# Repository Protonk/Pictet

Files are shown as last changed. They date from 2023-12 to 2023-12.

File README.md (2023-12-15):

# Pictet's Experiment

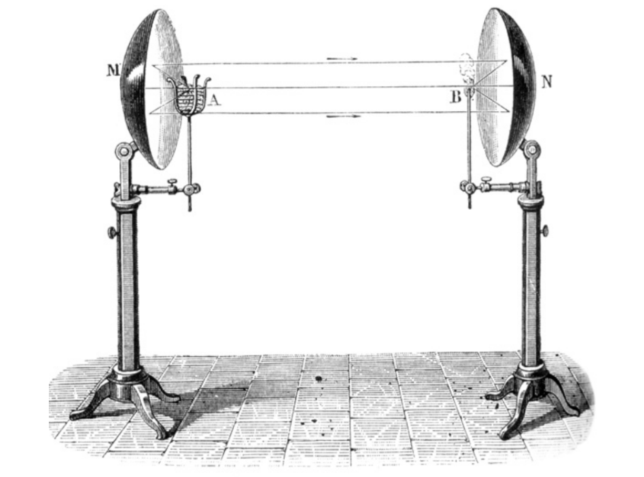
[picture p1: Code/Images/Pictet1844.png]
A lithograph of two parabolic mirrors on stands facing each other. The focus of one mirror has a basket of coals, the other kindling 1844 Apparatus


We are students of human-computer interaction who feel that speculation is important in the classroom. Speculating, failing, and then learning from our failure is how we innovate and advance as a society and grow as people. Science classrooms are important places for students to reason and speculate about the world, but sometimes they can feel intimidating to speak up in. We wanted to design a science demonstration focused on creating space for students to speculate about the outcome without fear of being wrong. Because we are not physicists or science teachers, rather than devising a new experiment, we decided to lift one out of some obscurity in the history of thermodynamics and show that through user research this experiment was still viable for classroom learning today, more than 200 years after it was first performed: [Pictet's Experiment](https://en.wikipedia.org/wiki/Pictet%27s_experiment), which showed the reflection of radiative heat by mirrors and the **apparent** reflection of cold.

We chose this experiment because despite a simplicity that allows it to be shown in a middle-school classroom, it can be surprising even to working physicists and students with experience with physics and heat transfer. It can accompany a discussion of blackbody radiation, visible and invisible light on the electromagnetic spectrum, or merely a discussion of what makes things hot and cold.

To accompany this demonstration we provide instructional materials in different modalities, designed through iterative user and concept testing of students' inclinations to speculate and reason about the outcomes. These are integrated into a short lesson plan with suggestions for staging and key questions to ask. We also offer guidance on how to implement the lesson, materials to support student engagement, and evidence for the impact of a learner seeing the demonstration for the first time.

## Contents

This project contains a capsule lesson plan appropriate for middle and high school science classrooms with a heat transfer component. The plan includes directions for constructing and conducting a demonstration, key concepts and questions for students, as well as a variety of optional discussion questions to allow the lesson to be tailored for student level and time allotted.

This lesson plan is released under a public domain license. Anyone may freely copy, modify or re-use the material we have created.

If you want to demonstrate this experiment in your classroom you may follow the links below.

- [Lesson Plan and Teacher's Guide](/Lesson%20Plan/Lesson%20Plan.pdf)
- [Experimental and Material Setup Instructions](/Lesson%20Plan/Experimental%20and%20Material%20Setup%20Instructions.pdf)
- [Resources for replication](/Excerpts/)

Read on for more information about why and how we put the lesson plan together.

## Why this project?

We did not want to make an app or design a change to how classrooms work. Science teachers don't need us or technology to help them understand that speculation is important. Classic experiments with [pendulums](https://www.aps.org/programs/outreach/physicsquest/past/swinging.cfm) are widely used to help students reason and speculate about concepts like mass, and science educators have been writing for [some time](https://pubs.acs.org/doi/10.1021/ed013p166)  about the importance of demonstration in the classroom.

We wanted to take advantage of our background as designers and researchers as well as the opportunity we had to conduct user and concept testing with students in order to attack a problem of narrow scope: a lesson plan that helps prompt speculation and inquiry in students, where the key stakeholders are limited to instructors themselves. This allowed us to focus on stakeholder needs and produce a solution that could be deployed today just as we have designed it.

### Doing research so teachers don't have to

Although Pictet's experiment was regularly demonstrated to students and included in at least one popular teacher's guide in the 19th century, someone today is likely to find it (if they find it at all) recorded as a curious footnote in the history of physics. Sandwiched between discussions of "frigorific rays" and "phlogiston", its value as a teaching tool is obscured. Further, finding pragmatic information about the demonstration such as suitable materials or valuable practices is a challenge and requires access to and a willingness to read paywalled journal articles for an uncertain benefit.

We suspected that middle and high school teachers were unlikely to see this as a good use of their time and we aimed much of our early secondary research at lifting Pictet's experiment out of this historical frame and collecting information about its use as a teaching tool into one place. This notion turned into our idea for our final deliverable for this project: a lesson plan. With our lesson plan, an instructor who discovers the experiment in one of those footnotes mentioned above and searches for more information will have, readily available, enough information to determine both the value of demonstrating it to their classroom and practical information about how to do so.

Teachers often have very few chances to test out additions to the classroom, but we could test and iterate on this specific goal with users throughout the design process. This allowed us to bring to bear our experience with user testing and validation to the problem of designing a lesson plan.

## Limitations

Because our solution is aimed at middle and high school teachers, the best user population is students of those ages. However, minors are always considered a vulnerable population for research (including class projects!) so all work must proceed through an Institutional Review Board (IRB). Given that the time frame for our project was less than 10 weeks, we moved forward by testing important elements of the lesson on a proxy–university students. On top of this limitation was a further one, we could not test users in an environment close to what we expected the lesson plan to be used in: a classroom. Our user testing was built around the recruitment of individuals for interviews and demonstrations.

Given these limitations, we approached user testing with the aim to first validate that our demonstration could create a space for speculation by the user and then to observe how user responses changed as the demonstration evolved. As the project went on and we continued to iterate on our prototypes, we put much of what is the lesson plan in front of users for validation and concept testing. However, the whole of the lesson plan could not be tested in the classroom environment we expect to see it used in.

Finally, we are not students of physics or working physicists. We feel experimental demonstrations of scientific knowledge must be carried out by scientists and non-scientists alike in order to broaden the scope and character of scientific knowledge. Our work in building the experiment and attending carefully to the user's behavior can offer lessons for science educators, not least of which is drawing attention to an experiment we believe has been unfairly neglected.

### Who we spoke with

We not only needed to read up on the experiment, but conduct user research as well. For example, our secondary research showed that Pictet's experiment was able to puzzle and surprise even well-educated physicists at the time, but we did not know if students today would react the same way. Would students who live in the modern world of heat lamps and infrared cameras still have their intuitions challenged? Did this experiment in fact create a space where students are able to speculate freely?

To answer these questions and others, we conducted user interviews with key stakeholders and moderated user testing with various iterations of prototypes, both of which we will explain in detail below.

#### Science Teachers

Our stakeholders for this project–the people who we hope will take up this lesson plan–are middle and high school STEM teachers. We conducted semi-structured interviews with three teachers via Zoom. One teaches in a well-resourced private school, one in a home-school co-op, and one via community science education programs. They were asked various questions regarding their perspective on demonstrating science experiments in front of students and general thoughts about the best way to create a space where students feel comfortable to speculate openly without the fear of being wrong or judged by their peers or teachers.

#### Student interviews

User interviews with undergraduate and graduate students were conducted as semi-structured interviews at the student union building at a local university. They consisted of questions asking about general perspectives and experiences about science classes and also specific questions regarding how different situations impacted their ability to speculate freely within the classroom. While we could not interview middle or high school students for our work, speaking with a mix of students inside and outside of STEM fields helped us understand how to consider students as a user group in general, rather than just speaking with instructors.

#### Capsule demonstrations

Once we conducted initial interviews with students, we prototyped virtual and in-person demonstrations with university students at the student union. Each demonstration included a short pre- and post- interview which we used to evaluate the effectiveness of the staging and presentation of the lesson.

#### Results

Through the synthesis and analysis of our qualitative data collected from the user and stakeholder interviews, the common themes and trends that emerged helped guide major design choices. For instance, our initial goal was to replicate the experiment and produce only a video to be shown in the classroom. While some of our stakeholders wanted options of how to demonstrate experiments to the class including simply showing a video, students prefer live demonstrations or hands-on experiments as opposed to watching a video. One student noted a common sentiment, saying "if this is something that can be demonstrated in person it would definitely be more interesting." This along with other discussions with students who preferred seeing and interacting with a demonstration even if they were not responsible for performing it, led us to produce a lesson plan with instructions on guiding the demonstration.

Another way that we involved the input of the interviews was with the worksheet handout that we included in the lesson plan. One teacher explained their philosophy of trying "to get students to make a prediction first as a way to engage more deeply with what's about to happen, especially if it's a common misconception that we are trying to reveal." This sentiment was echoed by a student who shared how they are: "[more comfortable with] 'write down what you think would happen' or make it anonymous [type of situations]." With this in mind, we crafted a hypothesis worksheet that had the students anonymously write down their hypothesis of what they thought was going to happen in the demonstration and why. Then after the demonstration, on the back of the same worksheet, it asks the students to explain what actually happened and what if anything was surprising to them.

## Takeaways

When we started on this project, lots of things were uncertain to us. We did not know whether or not students today would find the experiment counterintuitive or if it would provide space for them to speculate about the phenomena at work. We also did not know if we could recreate the experiment ourselves; how to integrate our secondary research about inquiry-based learning with our user research; or whether or not low and medium-fidelity prototypes would give good approximations to what we wanted to test.

Our first major takeaway from the project was that low-fidelity prototypes can work well in this space. Users, especially those we engaged in person, had less difficulty than we imagined understanding papercraft representations of the experiment, allowing us to effectively perform concept and user testing early on in the design process. Virtual demonstrations proved less effective in terms of eliciting speculation but still provided important feedback which we incorporated into our design.

Another takeaway came from the nature of the user tests we were able to perform. We discovered in our user and stakeholder interviews that students preferred to give speculations and hypotheses first in private or in small groups before volunteering these ideas to the whole class. Motivated by this, we developed worksheets to go along with the lesson plan where students can record speculation privately. However, our user testing was almost exclusively one-on-one, and users were understandably reluctant to write detailed feedback during user tests–preferring to offer it verbally. This meant that while we have good evidence from user and stakeholder interviews on the value of private, written speculation in these scenarios, we were limited in how we could assess our solution here.

## Future work

The limitations noted above offer clear signs for future work. Our next steps for the lesson plan are:

- Seek out Institutional Review Board (IRB) approval to demonstrate and assess the response of our intended user group (middle or high school students) in a classroom environment.
- In collaboration with stakeholders, develop assessments for student learning during the demonstration. As one of our stakeholders noted, "Most of the learning is answering post-lab questions."

Aside from these major improvements, our lesson plan is available here on GitHub, where comments and suggested changes can be continuously integrated. The lesson plan and associated materials are shared under a free license so anyone can copy, adapt, and re-use what we have created for their classrooms.

Contributions are welcome!

## Just who is we?

* This project is the work of [Adam Hyland](https://adampunk.com) and [Daniel Teramoto](https://www.linkedin.com/in/daniel-teramoto/), students at the Human Centered Design and Engineering department of the University of Washington.

## Acknowledgements

This project was produced in Dr. Daniela Kim's User Centered Design course. We are grateful for her feedback and support as well as the support of our awesome TA Brian Kinnee. Thanks also to Dr. Brock Craft for assistance with fabrication.

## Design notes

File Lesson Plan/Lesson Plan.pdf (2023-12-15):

# The Third Heat: Pictet’s Experiment

## Intro

Let us think for a moment about how heat appears to us as a sensation. We can feel what we know of as conduction–A hand on a hot pan. We can feel convection–a fire warming a room. But we also sense a different kind of heat. When opening a furnace door we feel heat IMMEDIATELY, much faster than air molecules around the furnace could reach us.

We also feel the heat of the sun. Stepping out of full shade on a hot day makes things immediately hotter. How does that work? Is that energy we experience part of the light we can see? The sun is certainly bright, and so is a hot furnace. But plenty of hot things don’t emit light. Humans are pretty warm and we don’t visibly glow. Neither does a hot pan one might reach for.

Let’s travel back in time to 1790. We don’t know that the light we see is just a tiny slice of a broad spectrum of energy, most of which is invisible to us. It is ten years before the first bit of this spectrum outside our visual experience will get isolated and examined scientifically.

What we have is a suspicion that beyond conduction (touching that hot pan), and convection (feeling the heat of a fire roil through the air), there is a third heat, one which travels quickly like light. To turn this suspicion into knowledge, scientists turn to experiments. We are going to conduct one today like it would have been done 230 years ago.

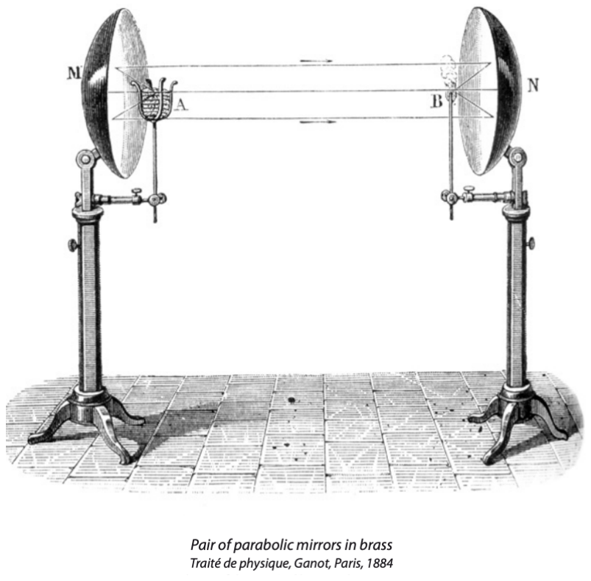
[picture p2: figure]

## The Science Behind Reflection of Heat

Pictet’s experiment is the name given to a series of experiments performed in 1790 by Marc-Auguste Pictet which demonstrated radiative heat transfer and reflection of radiated heat from objects that were not visibly glowing, ten years before the isolation of infrared light from sunlight and half a century before modern theories of black-body radiation were developed.

After measuring an increase in temperature from the reflected heat of an object, a colleague suggested to

Pictet that he insert a very cold object and see what happens. Snow was brought into the laboratory and placed where the hot object had been. To Pictet’s surprise, the temperature of the thermometer went down.

Some scientists at the time struggled with this result because they held a misconception noted in students of heat transfer today, that cold objects–those which feel cold to the touch–emit or radiate coldness akin to how we sense radiant heat from hot objects. Others, who knew that cold was the absence of heat, incorrectly inferred from this that the temperature should remain the same, and had to update their intuition.

The experiment was a way to move beyond apprehending radiant heat with our senses to measuring it with tools. What we would now call heat flux from an object could be reflected by mirrors, and focused following the same rules of optics that visible light did. Infrared cameras like those on the James Webb Space Telescope that today help us peer further into the past than we have seen before operate on principles demonstrated here.

### Suggested placement of the lesson

The demonstration of Pictet’s experiment can be useful for a range of students. This lesson plan has been designed to allow instructors the option to teach the material at a variety of levels. While the key question, “how is heat reflected and focused by mirrors” is relatively simple, the questions the demonstration prompts students to ask can be productive even for students with a fair amount of experience in physics.

For middle school science students learning about modes of heat transfer, the demonstration can prompt students to inquire about the role and nature of radiative heat transfer. Those classrooms may choose to skip questions about the determination of the focal point and questions about how much thermal radiation is collected by the mirrors. However, a review of these principles can be achieved without calculus and only some trigonometry

1
. Further, while
heat flux impinges on an area, the discussion can be simplified by considering only a two-dimensional mirror and object setup.

While not covered directly in this lesson plan, asking students to consider different material choices for the hot object can prompt discussions about the relative role of emissivity and reflectivity of objects with respect to radiative heat transfer, a subject with concept inventories have shown to be a common source of student misconceptions.

1 We assume spherical mirrors and only consider objects at the focal point of these mirrors, simplifying the calculations.

## Key Terms

Focal Point: The point at which parallel light rays passing through a lens or reflected from a curved mirror converge, or the point from which they appear to diverge after refraction or reflection by the lens or mirror. Also called the focus or the principal focus.

Concave: Curving inwards. A concave mirror is one in which the reflecting surface is formed from the interior surface of a sphere or paraboloid. For this lesson, we treat all concave mirrors as spherical.

Black-body radiation: Thermal radiation emitted by an ideal, non-reflective object, dependent only on the object’s temperature.

Infrared: Electromagnetic radiation just below the range of visible light. Sometimes referred to as “thermal radiation” or “radiative heat”.

Conduction: The process by which heat is directly transmitted through a substance when there is a difference of temperature or of electrical potential between adjoining regions, without movement of the material.

Convection: Movement caused within a fluid by the tendency of hotter and therefore less dense material to rise, and colder, denser material to sink under the influence of gravity, which consequently results in the transfer of heat.

Radiative heat transfer: Transfer of energy via thermal radiation, i.e., electromagnetic waves. This occurs across a vacuum or any transparent medium (solid, fluid, or gas). Thermal radiation is emitted by all objects at temperatures above absolute zero, due to random movements of atoms and molecules in matter.

## KEY QUESTION:

## How is heat reflected and focused by mirrors?

## Getting Started

The goal of this lesson is for students to understand Pictet’s counterintuitive science experiment first performed in 1790, showing the reflection of radiative heat by mirrors and the apparent reflection of cold. Some main objectives are to encourage the students to be creative, to think like scientists and engineers, and to give them a space where they are free to speculate about the results of the science demonstration without having the pressure of saying their guess in front of their peers.

Materials Needed:
- 2 concave mirrors
- 1 temperature sensing device
- A hot object
- A cold object
- Objects to hold the concave mirrors, thermometer, and heat source in place

If you do not have the exact materials, you can follow our associated experimental setup document which provides budget-friendly alternatives for how to demonstrate the experiment best.

### Demonstration Setup

See the associated experimental setup document.

## Safety

The experiment uses hot and cold objects. The simplest hot object to use is a candle–precautions for handling open flame are required. A glass of ice water is sufficient for a cold object, but the effect will be more dramatic the colder the object is. The use of dry ice or liquid nitrogen to cool a metal object requires precautions in the classroom.

### Before starting the demonstration with students, consider these questions

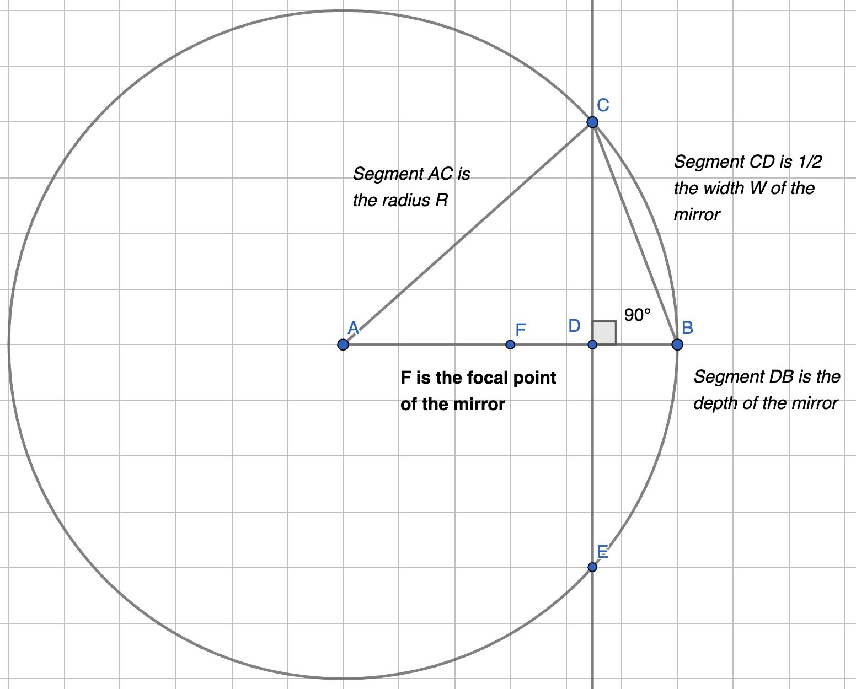
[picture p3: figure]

How do light rays reflect off concave
mirrors?

In setting up and discussing the experiment, discussing how visible light is reflected by mirrors can motivate where the objects and thermometer are placed relative to the mirrors. For concave mirrors, light radiating from the focal point of a mirror will reflect perpendicular to the axis of the mirror. Calculating this focal point, because it comes from these nearly parallel rays, can use the small angle or paraxial approximation, and no calculus or overt trigonometry is needed. The distance of the resulting focal point F is F = R / 2 where R is the radius of the imaginary sphere that the mirror forms a part of.

If a light bulb is placed at the focus of a spherical mirror, a cone of that light is collected in the mirror and reflected in a beam. But the light from which isn’t captured by the beam falls off with the square of the distance from the source. This is how the headlights of a car can shed light at a distance but the same light held in the air would illuminate only a short distance.

What are the ways we can feel the sensation of heat?

This is a broad question that can be answered by students from their experience. Prompt them to think about touching hot objects and feeling the heat of a fire to get them to think about conduction and convection. For radiative heat transfer, this may require some additional prompting. Students may or may not have experience with a furnace or kiln—if they do, ask about how quickly they feel the heat from these objects at a distance. If they do not, prompt them to think about stepping into the sun on a windy day. The heat felt in that scenario cannot be via convection and must come from something else.

Does heat bounce off mirrors like light rays?

This can be posed to almost any student. After discussing the above, prompt students to think about roasting meat or vegetables. We often “tent” a roast by wrapping it in foil. What purpose might this serve? After removing a hot object from the oven, it will cool to room temperature if left alone. Covering the object in foil insulates it. If heat is transmitted via conduction or convection alone, it might serve to wrap an object in paper. Why do people use foil in their kitchens instead?

This question can be extended to a discussion of the characteristics of an object, specifically emissivity and reflectivity. However, for classes that have not discussed these topics, a general discussion can still be valuable.

Does the transfer of “cold” exist separate from the transfer of heat?

The range of human sensation provides an important anchor for understanding the world, but it can mislead us. We tend to think of objects that are warm to the touch as “hot” and those that appear cold as “cold” and students can hold the misconception that this split in sensation means a split in function or behavior.

One way to motivate questions like these can be to hand out cold packs that have just come out of a freezer as well as cold packs that have been allowed to come to room temperature. Objects at room temperature will not cause a strong sensation but cold objects will.

Another way to move this question forward is to have students discuss the implications of a hypothesis that cold objects emit or radiate coldness. If an object “gives off” cold, does a colder object give off more? Does a hot object also give off cold? When might an object stop giving off cold and instead give off heat? Probing questions like these can help students steer themselves to a conclusion that heat transfer occurs across a difference in temperature, rather than being connected to the sensation of hot and cold.

What is black-body radiation?

Where the demonstration is performed with a heated object (not a candle), students can be prompted to inquire about what features of the object aside from its temperature determine the amount of thermal energy transmitted. A “perfect” black-body emitter will give off the maximum amount of energy at a given temperature, while an object painted white will give off far less.

A comparison of those two situations is not the only question that can be posed. One of the key goals of the original experiment was to determine whether or not an object that was not visibly glowing gave off thermal radiation. In the “hot” stage, this can be shown with a hot object, but in the “cold” and “reset” stages, radiation of heat from the thermometer to the environment is observed. Here students can see that something that is roughly room temperature can radiate heat.

### Setting the Stage: Fostering Inquiry-Based Learning

Prior to demonstrating the experiment–either during class or as a take-home assignment beforehand–distribute the attached hypothesis worksheet. The questions ask students to make simple predictions about the behavior of the system during the experiment. The main goal is to get students to advance a prediction and articulate their reasons why they did so.

Once you have the demonstration set up, responses in class work best in small groups. Even though for practical purposes there will likely be only one demonstration in the classroom, student reflection and discussion in groups helps them advance and process speculation about the outcome.

Have the students discuss amidst their group and decide which hypothesis they think is best. Make sure that each group has a spokesperson for their group that can share their hypothesis’ -science happens in community!

Next, have a class discussion where each team reflects to the class their hypothesis and discuss in class the potential consequences of each. After demonstrating the experiment with a hot object, ask groups to review the outcomes and report on how the system behavior deviated from what they expected. Most groups are likely to produce a “correct” answer at this stage–ie a hypothesis that says that the temperature at the sensor will go up with a reasonable explanation as to why.

When you repeat this process with the cold object, answers are more likely to vary both in predicted outcome and rationale.

## Demonstration of the experiment

The demonstration has roughly three stages: hot, reset, and cold.

Pictured is the setup for Pimpas et al. (2017), which recreated the experiment using a candle and a thermocouple.

### Hot:

Place a hot object in the focus of one mirror and ask students to pay attention to changes in the temperature sensor at the other focus. The temperature should increase
immediately (if slowly) when the hot object is
placed in the focus.

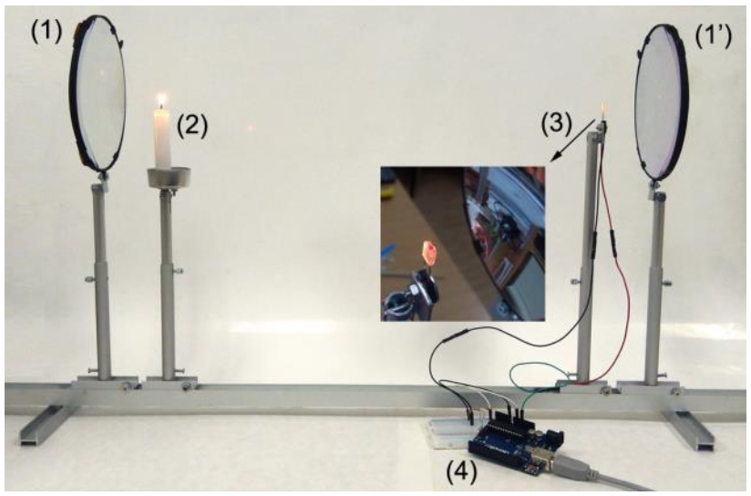
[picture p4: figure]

At this stage, one common student misconception is that the hot object is heating the sensor simply due to proximity rather than via reflection of radiant heat by the two mirrors. There are two interventions which can be useful here.

You may remind students of the inverse square law for radiation–the heat flux for a given area at a 10 cm distance (the distance from the hot object to the mirror) will be ~80 times the heat flux for the same area at 90 cm distance (the distance from the hot object to the thermometer for a 1 m distance setup). This has the advantage of allowing you to prompt discussion and computation of the relative heat flux.

There is a more direct route at this point, however. While the hot object is in focus, slide an opaque object between the hot object and its mirror (a sheet of printer paper will do). This has the effect of blocking all radiated heat from reaching the mirror but leaving the side facing the thermometer clear. If it was proximity to the heat source, not reflected radiant heat which caused the temperature increase the temperature should be expected to continue to rise. Instead, it can be observed to fall.

### Reset:

After removing the hot object, have the students observe that the sensor returns to room temperature. The sensor will transfer heat to its environment until it is at thermal equilibrium.

This stage is a place to prompt students for discussion of what that environment is for the sensor. When heat is transferred in the form of infrared radiation, a portion of that reaches the mirror and is reflected. That reflected portion is lost to the environment without something in the other focus.

### Cold:

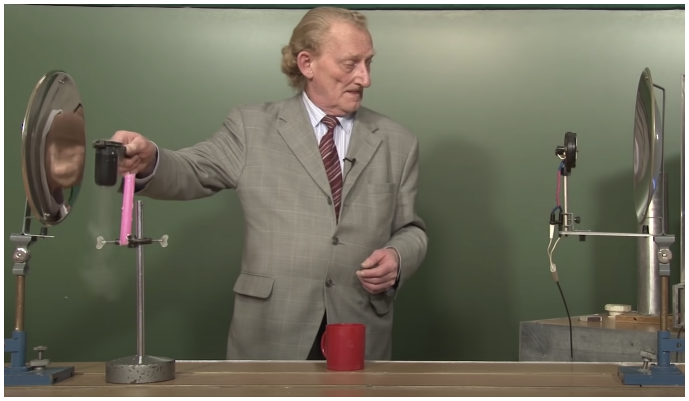
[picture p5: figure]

Demonstration of a cold object placed near the focal point of the left mirror. Note the rough positioning of the cold object and the precise positioning of the sensor.

Once the sensor is at room temperature, ask students to make a prediction as to what will happen when a cold object is placed in the other focus. Defer the question as to why until after the demonstration.

After placing a cold object in the focus, observe carefully the change in temperature at the sensor. The decrease in temperature will be less than the increase with a hot object. For a water-ice object at ~ 0 ℃ the change will happen slowly. With an object cooled well below 0 ℃ it will happen faster. However, the temperature should go down.

After students observe the drop in temperature, you can insert a piece of paper between the cold object and its mirror just as you did the hot object. The temperature at the sensor should rise.

At this point, you should ask student groups to speculate why the introduction of the cold object causes a temperature drop at the sensor. Remind them of their explanations as to why a hot object caused the temperature to go up.

## Discussion

There are a few ways to motivate discussion of an explanation of why the temperature at the sensor drops.

Ask students to imagine a different setup: a temperature sensor in a bath of liquid where a cold object has been inserted. In this thought experiment, the temperature of the bulk fluid will drop until it reaches equilibrium. This sidesteps the question of reflection but prompts students to imagine the sensor as part of a system.

Remind students that one phenomenon shown by the hot object demonstration and the reset is that all objects radiate some heat to their environment. Setting up the mirrors as we did means that some portion of that radiated heat is captured by the mirrors. With no object in focus, all radiant heat passing the focus comes from the environment. When a cold object is placed in the focus instead, the portion of that heat flux that would otherwise be reflected by the mirror is greatly reduced.

Because the features of the experimental setup are known, the above discussion can also include a calculation of how much of the system is comprised of the two mirrors.
- The fraction of the circle with center F and radius R/2 (arc CBE in the above diagram) can be computed by doubling the angle FCD.
- Angle FCD can be computed by taking the inverse tangent of (W/2)/(F - depth). The distance F, depth of the mirror, and width of the mirror are known. For a mirror with a depth of 0.51 cm and a width of 9 cm, the focal length is 10 cm, which gives an angle of ~30 degrees. Doubling that leaves 60 degrees.
- Dividing this from the imaginary circle around the temperature sensor gives the proportion of the radiation leaving the sensor which reaches the mirror. It also gives, conversely, the rough proportion of thermal radiation reaching the opposite mirror which will be focused on the sensor. For our example mirror this is 1/6th of the total radiation in the system.
In effect, a cold object will radiate much less heat than the surrounding environment over the arc CBE that is focused on the sensor. Without an object in focus, this radiation comes entirely from the environment which at the start of the demonstration is in equilibrium with the sensor.

## Related heat transfer concepts:

- Temperature vs. Heat – Concept inventories from Jacobi et al. 2003 and Prince et al. 2012

## Corresponding Extension Activities

Hypothesis Worksheet (https://docs.google.com/document/d/1h0e2V8rjzgdIdF8Y1Anfe79y_mKV-JDIVFuxmbnc7zM/edit?usp=sharing)
Suggested Diagrams Handout (https://docs.google.com/document/d/1ZkofCvViEXuZQal_lcj62aqwQ9KTNLxvEdXssA_OUmA/edit?usp=sharing)

## Suggested Resources

- Pictet’s experiment (https://en.wikipedia.org/wiki/Pictet%27s_experiment) on the English Wikipedia created for this lesson covers historical context for the experiment and links to peer-reviewed sources.
- "Are There Rays of Cold?", (https://www.youtube.com/watch?v=mW4T0ZaiGno) an undated video demonstration in Russian released in 2015 from the Moscow Engineering Physics Institute.

## References

### Concept inventories for heat transfer

Prince, M., Vigeant, M. and Nottis, K. (2012), Development of the Heat and Energy Concept Inventory: Preliminary Results on the Prevalence and Persistence of Engineering Students' Misconceptions. Journal of Engineering Education, 101: 412-438. https://doi.org/10.1002/j.2168-9830.2012.tb00056.x

A. Jacobi, J. Martin, J. Mitchell and T. Newell, "A concept inventory for heat transfer," 33rd Annual Frontiers in Education, 2003. FIE 2003., Westminster, CO, USA, 2003. https://doi.org/10.1109/FIE.2003.1263338

### Recreations of the experiment

Evans, James; Popp, Brian (1985). "Pictet's experiment: The apparent radiation and reflection of cold" (http://webspace.pugetsound.edu/facultypages/jcevans/Pictet's%20experiment.pdf) (PDF). American Journal of Physics. 53 (8): 737–753.

Pimpas, Alexander; Mihova, Gergana M.; Andreeva, Andreana I.; Zografov, Nikolay N. (2017). "Trapping Radiant Cold Via Mirrors" (https://jpt.uni-plovdiv.bg/wp-content/uploads/2019/04/Pimpas-J.-Phys.-Technol.-1-2017-65-69.pdf) (PDF). Journal of Physics and Technology. 1 (2): 65–69.

### General Reference

Lemons, D. S., Shanahan, W. R., Buchholtz, L. J. (2022). On the Trail of black-body Radiation: Max Planck and the Physics of His Era. United Kingdom: MIT Press. ISBN: 9780262047043

The Pictet Cabinet: The art of teaching science through experiment (http://institutions.ville-geneve.ch/fileadmin/user_upload/mhn/images/votre_visite/site_mhs/aide_pictet_e.pdf) (PDF), a 2011 pamphlet from the Musée d'histoire des sciences de la Ville de Genève (https://en.wikipedia.org/wiki/Mus%C3%A9e_d%27histoire_des_sciences_de_la_Ville_de_Gen%C3%A8ve) (Museum of the History of Science of the City of Geneva)

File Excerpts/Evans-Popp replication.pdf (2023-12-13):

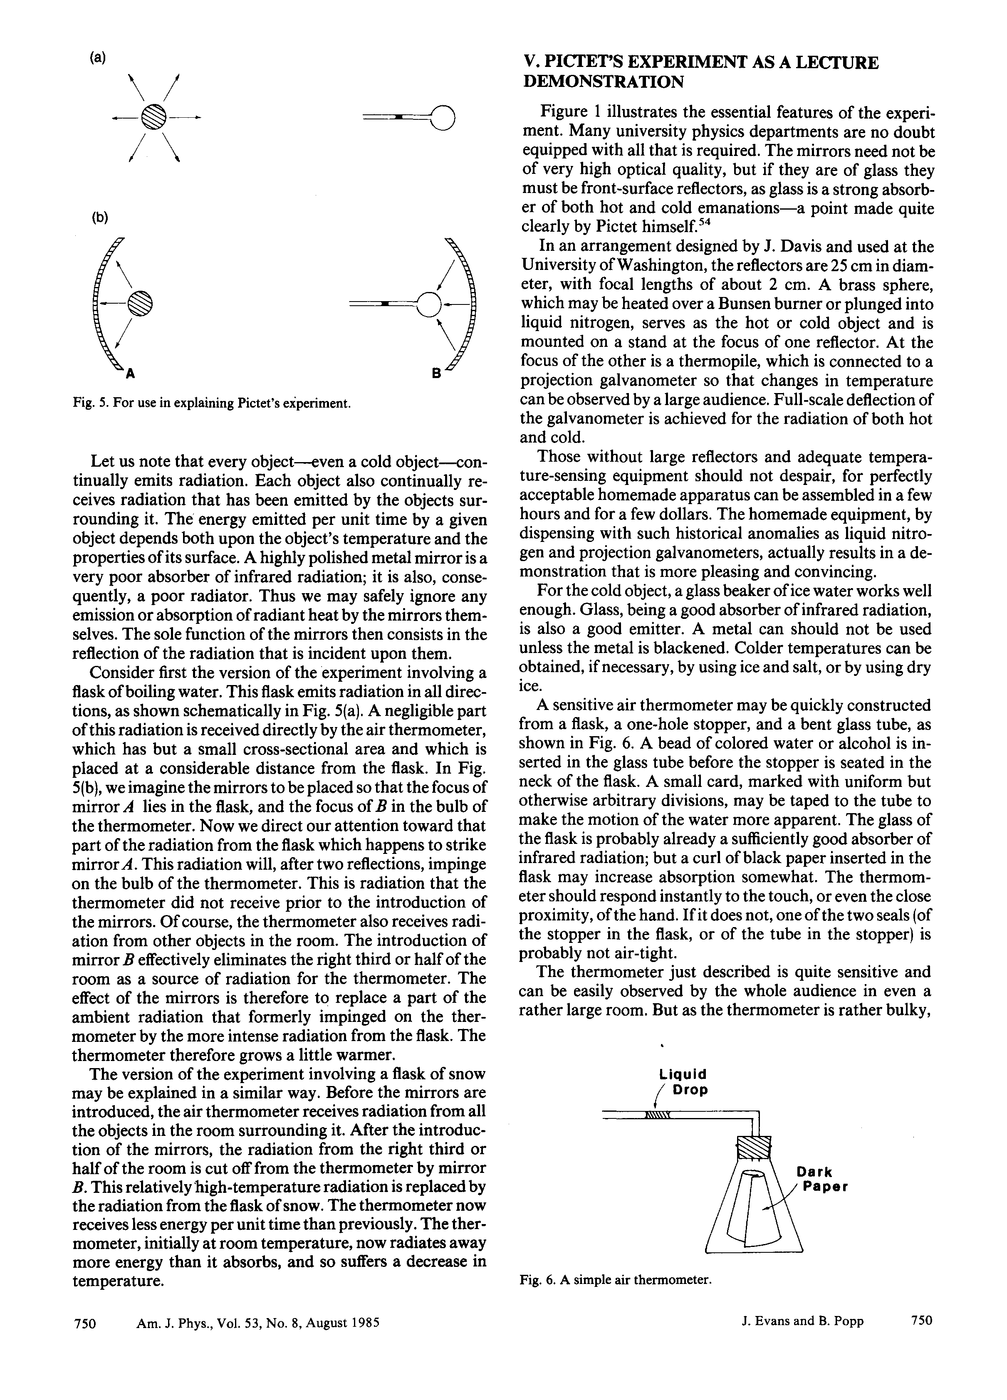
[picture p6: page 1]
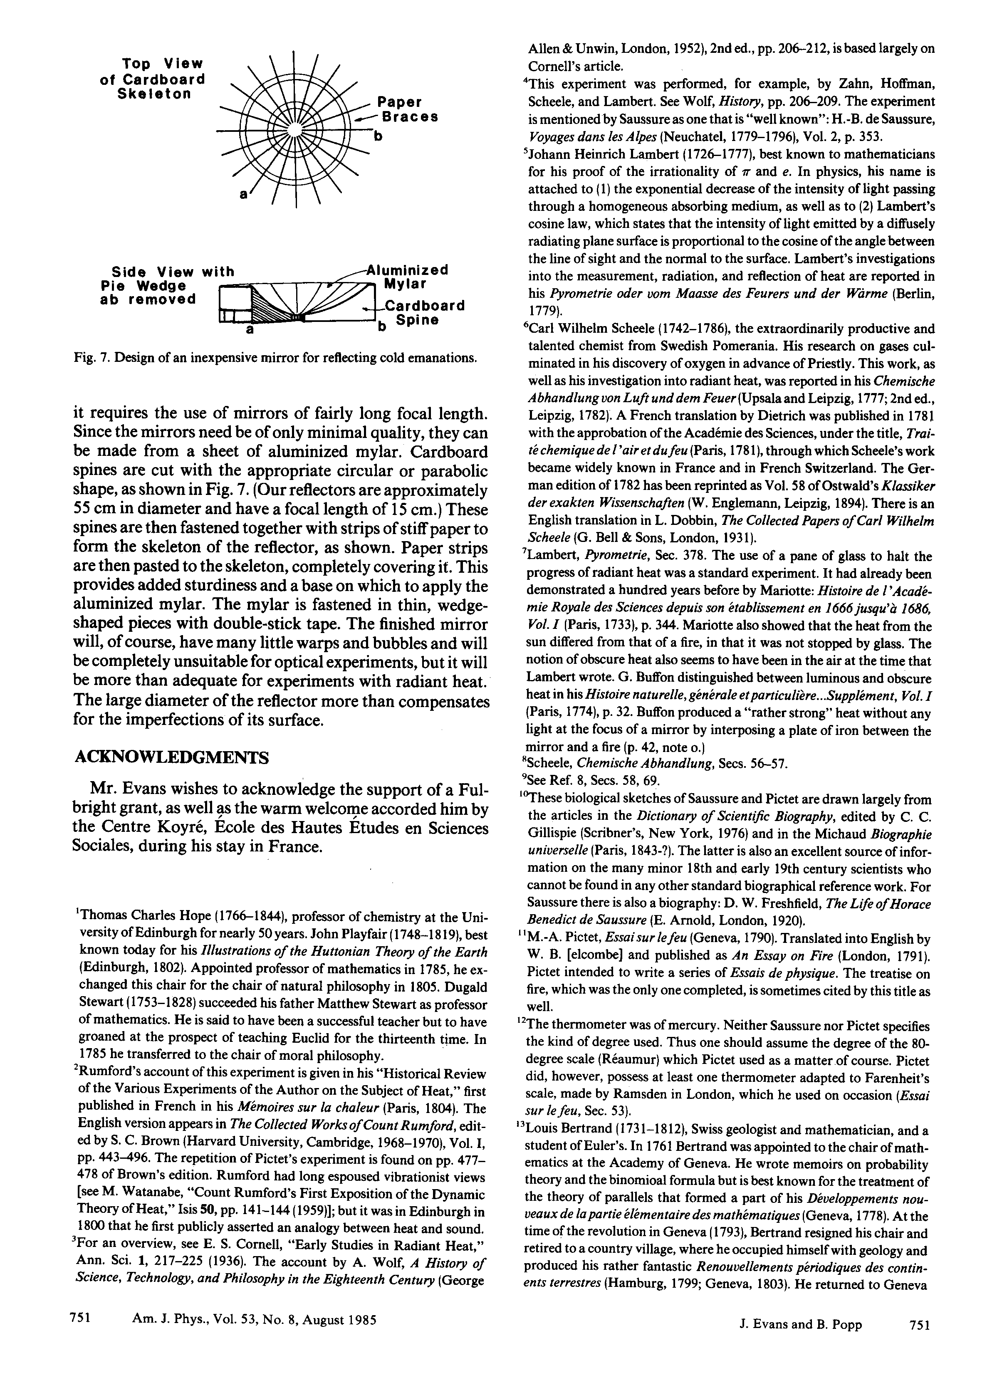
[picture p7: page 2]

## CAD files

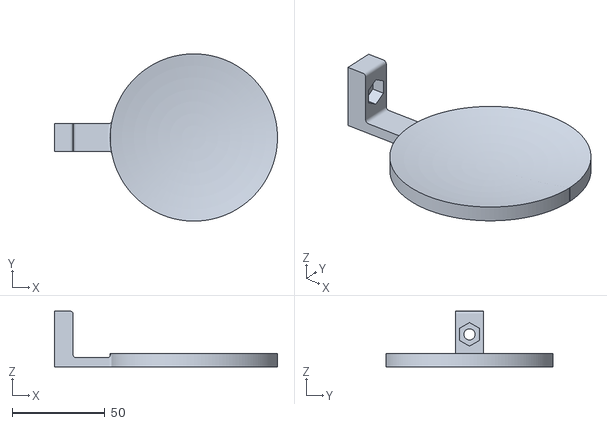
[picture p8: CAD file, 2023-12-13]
Code/CAD files/concave-mirror-9cm.stl
120.0 x 90.0 x 30.0

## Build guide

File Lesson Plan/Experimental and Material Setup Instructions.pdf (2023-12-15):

## Experimental and Material Setup Instructions

### Introduction

The experiment involves the observation of reflected radiant heat, first from a hot or heated object to a temperature sensor and then from a temperature sensor to its environment. The magnitude of the effect observed depends on two main factors:
1. The amount of energy released as radiant heat by the hot object or thermometer
2. The proportion of that energy reflected and transmitted by the mirrors the system
The greater the magnitude of this effect, the more temperature deflection is seen by the sensor. An increase in energy released can be achieved by heating an object with a given emissivity to a higher temperature and an increase in the energy reflected can be achieved through mirrors which capture a larger fraction of the heat radiated by the object (larger mirrors or mirrors with a longer focal length will capture more of this radiation, see below)

During the performance of the “hot” stage of the demonstration, the effect is strong enough to be observed even with a relatively less sensitive system; however, the effect in the “cold” stage is less dramatic, and less sensitive setups may require more time to observe a change.

## Setup

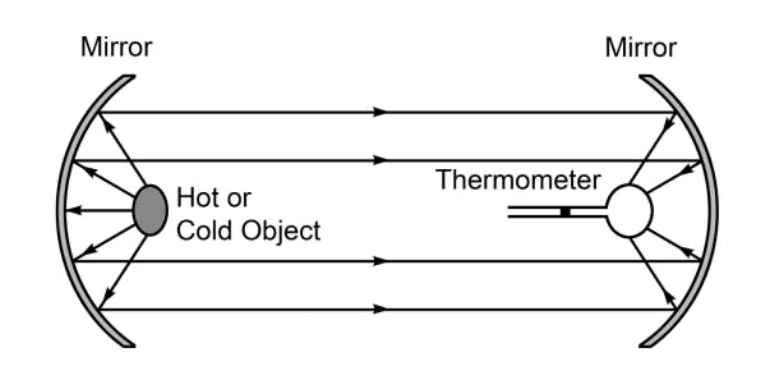
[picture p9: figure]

Diagram of setup from Pimpas et al. 2017

The two concave mirrors are set up at a distance of 1 to 2 meters

1
facing one another
perpendicular along their optical axes. At the focal point for one mirror, a temperature sensor is fixed. The focal point of the other mirror is where the hot or cold object is placed.

Our suggested hot and cold objects are large enough that they need not exactly be at the focal point, but the target size of thermometers is small.

Determination of the focal point can be made during the experimental setup using visible light by placing a light bulb at the focus of one mirror and aligning the temperature sensor at the point where the visible light is focused by the other mirror.

Mirror sizing
The purpose of the mirrors is to collect light to or from a focal point. A larger mirror will collect relatively more heat than one with a smaller diameter, and a deeper mirror will collect more than a shallow mirror of the same diameter. This experiment has been replicated with mirrors of diameter 8-25 cm with varying focal lengths. Larger and deeper mirrors will collect more heat flux and allow for the use of less sensitive temperature sensors.

The distance to the focal point can be determined from the width W of the mirror and its depth

D. Knowing those, the focal length is ((W/2) | . For our supplied instructions

2
+ D

2
| ) × (1/4D)
for a 16 cm wide mirror with a depth of 1.67 cm, the distance is 10 cm.

Mirror material and dimension
This experiment has been performed in modern times with three kinds of mirrors:
1. Mirrors made from a structural backing material coated in aluminum or Mylar. Physicists at the University of Washington cut cardboard ribs to the desired size and arc and covered them with Mylar. We created mirror structural backing in a 3D printer, sanded the surface, and applied high-gloss aluminum spray paint.
2. Silvered glass mirrors. Researchers at Sofia University in Bulgaria used small mirrors for their recreation. They did not report the dimensions of the mirror but we used small commodity concave mirrors purchased on Amazon.
3. Formed polished metallic mirrors were used by instructors at the Moscow Engineering Physics Institute for their recreation. Not having access to these we did not attempt to replicate this choice.
The size and shape of these mirrors differ. UW physicists used deep 55 cm diameter mirrors with a focal length of 15 cm, while those at Sofia University used what appears to be shallow, ~ 10 cm mirrors. As noted above, the size and shape impact the amount of infrared radiation reflected, but the material choice also has an impact. However, both Mylar tape and aluminum spray paint have very high values of reflectivity and should be appropriate.

1 Distances shorter than 1 meter run the risk of implying to students that the hot and cold object is influencing the temperature sensor by simply being near it. Longer distances are possible, but errors in position and orientation grow with distance.

Evans and Popp 1985 p. 751 contains instructions for the creation of a cardboard mirror backing, seen here:

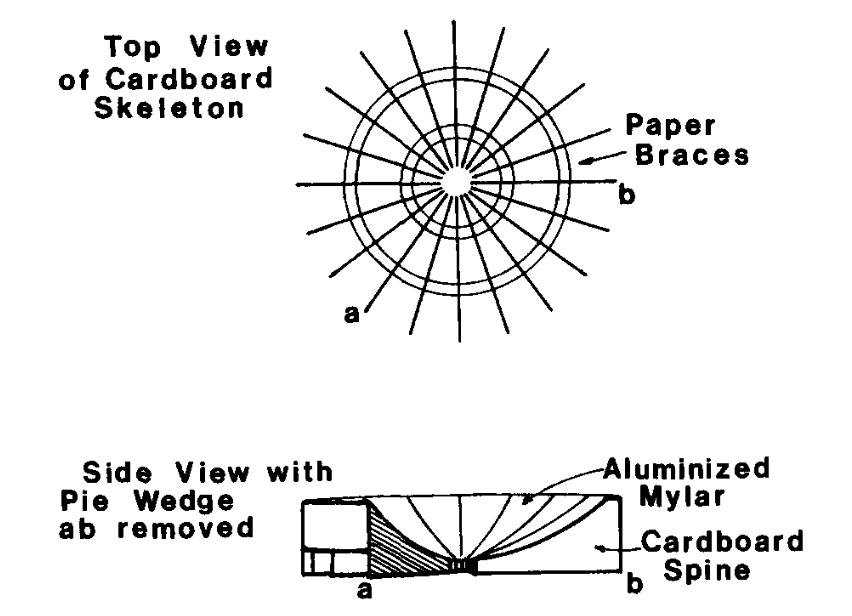
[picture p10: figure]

For a width of 55 cm and a focal length of 15 cm, the desired depth of the mirror is roughly 18cm.

Temperature sensor
The temperature-sensitive instrument may be a consumer-grade digital temperature sensor (e.g. the MCP9808 which has a precision of 0.25 ℃ over 2 seconds), a mercury thermometer, or a thermocouple. University of Washington physics teachers constructed galvanometers in 1985.

The choice of sensor is linked to other choices. In general, larger and deeper mirrors will require less sensitive instruments as will very hot or very cold objects. If you are planning to use relatively small mirrors and cold objects at the temperature of water ice, a sensitive thermocouple might be better than a digital temperature sensor.

A major advantage of the thermocouple and digital sensor over a mercury thermometer is the ability to transmit the results to a display. An advantage of a thermocouple over either choice of thermometer is relatively higher

2 sensitivity, while thermometers in general have the advantage of interpretability. With a thermocouple, students must be introduced to the system of measurement and must recognize that a deflection in current represents a deflection in the instrument.

2 Most commodity thermocouples have a rated temperature sensitivity similar to the MCP9808, but in our experience deflections in temperature less than the rated sensitivity can reliably be observed.

Hot objects
One of two options has been used in the modern recreation of the experiment
1. A metal sphere or slug roughly 2-3 cm in diameter heated to more than 200 ℃. Much larger and it will occlude too much of a 9 cm diameter mirror. Smaller and it will have reduced heat capacity.
2. A small open flame, for instance, a candle or a Bunsen burner.
The original experiment showed objects radiated heat at lower temperatures as they seemed to radiate heat and light at very high temperatures. This is one of the earliest experimental demonstrations of black-body radiation, decades before much of the theory was developed in the mid-19th century. The use of a candle for a hot object is much simpler, but it will not allow you to as easily demonstrate black-body radiation, because the candle flame is also emitting visible light.

Cold objects
Two options are available:
1. Using water ice, including snow or a glass of ice water at roughly 0 ℃.
2. Cooling an object with a refrigerator, dry ice, or liquid nitrogen to temperatures well below 0 ℃.
A colder object will show a relatively more dramatic effect. An object cooled with liquid nitrogen can be roughly -190 ℃ and will emit much less heat through radiation than the same object cooled to 0 ℃. However, the effect can be demonstrated with a sensitive thermometer even with a glass of ice water.

## Material cost estimates

A variety of material choices were presented with the possibility that some classrooms may have access to certain elements of the apparatus available. Choices of mirror, heat source, and temperature sensor can be mixed and matched based on what is on hand or available at low cost. Estimates of material cost for sensors and mirrors are below, rounded to the nearest dollar.

Mirrors:
- Concave mirrors are available on Amazon. We used 10 cm mirrors (https://www.amazon.com/dp/B079836VBW?psc=1&ref=ppx_yo2ov_dt_b_product_details) with a focal length of 15 cm: $24
- 3D printed mirror cost feedstock for 16 cm mirrors: $2
- We used recycled cardboard and paper. New cardboard for a roughly 20 cm diameter mirror: $6

Sensors:
- MCP9808 High Accuracy I2C Temperature Sensor Breakout Board, (https://www.adafruit.com/product/1782) available from AdaFruit: $5
- 0.56" 4-Digit 7-Segment Display w/I2C Backpack - Yellow, (https://www.adafruit.com/product/879) available from AdaFruit: $10
- Stainless Steel thermocouple, (https://www.amazon.com/Thermocouple-Sensitive-Application-Temperature-Measurement/dp/B0C3Z8H29N?th=1) available from Amazon: $13

## Material instructions and links

Project materials and code are available on Github in the public domain: github.com/Protonk/Pictet. This repository also contains an excerpt from Evans and Popp 1985 detailing their experimental replication, shared as fair use.

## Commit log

2023-12-13 add files and code
    [concave-mirror-9cm.stl]
2023-12-15 make live
    [concave-mirror-9cm.stl]
